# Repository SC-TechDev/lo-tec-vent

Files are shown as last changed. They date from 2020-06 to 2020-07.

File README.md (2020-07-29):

# LoTec Emergency Ventilator Concept - June 6, 2020

This ventilator concept builds on the mechanically actuated Bag-Valve Mask (BVM) designs originally developed at MIT as the [MIT Emergency Ventilator E-Vent](https://e-vent.mit.edu)

The materials provided include engineering drawings, descriptions, photos and videos of designs and proposed production techniques for ventilators Steelcase developed for possible use as part of COVID response actions. Steelcase has not completed the work to validate this design, reviewed these materials with FDA or any other government agency or produced any ventilators. We invite you to use these materials to the extent they are useful in designing and making similar products. However, be advised that these drawings and other materials have not been reviewed by FDA or any other government agency or evaluated for safety or effectiveness for use with any medical condition. We are making these materials available as part of our response to the COVID emergency. Steelcase disclaims any liability for any products made by others using these designs and production techniques. Each user must make their own assessment about the suitability of the design for their particular use.

## Design Goal

The specific goal of this design is to simplify manufacturing and reduce costs and complexity. This is especially relevant in developing countries where servo motors and electronic controls may difficult to procure and maintain. We replaced the servo motor, control board, and electronic user interface with a simple speed-controlled DC motor and adjustable mechanical linkages. This design consists of a standard windshield wiper motor or equivalent connected to a series of mechanical linkages. The steel linkages are assembled with common screws, pins and bearings. The entire unit can be built with standard metal fabrication processes. We improved the user interface with 3D printed handles and covers.

## Proof Of Concept

The following information describes the operation of the ventilator. A prototype was built to prove the concept of the adjustable mechanical linkage. This design is not ready for production or implementation. It does, however, prove that the linkages delivered the desired performance requirements and that the user controls can be simple and intuitive. Further refinement of the design is required to improve durability, manufacturability, and reliability.

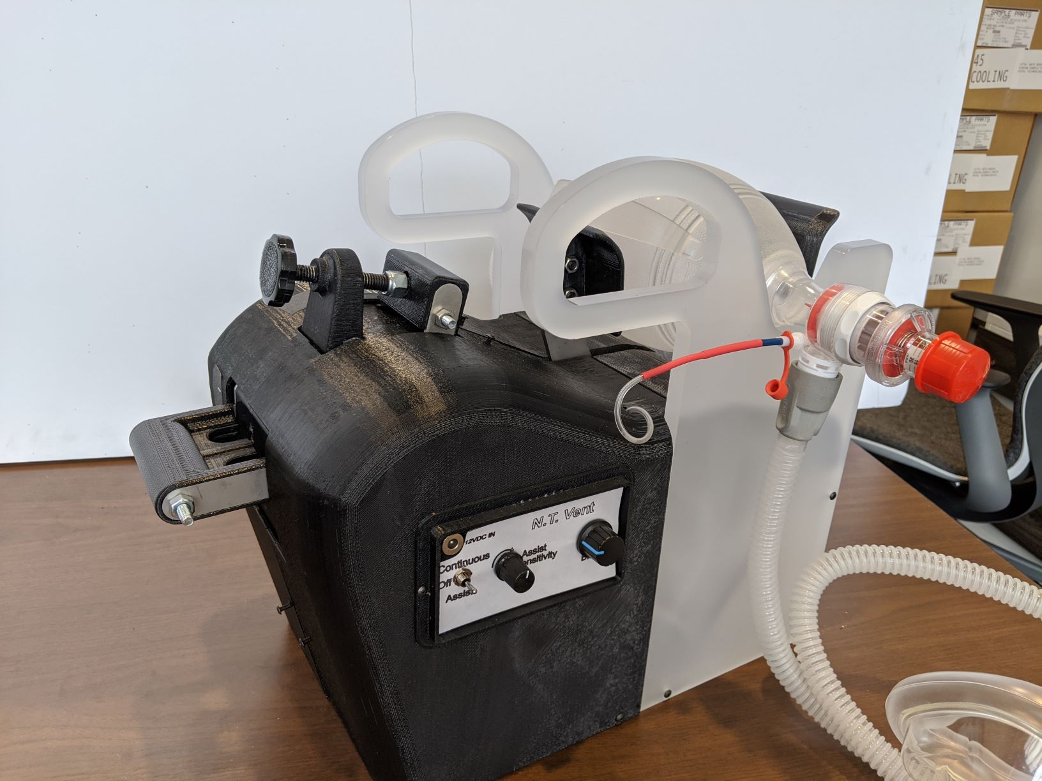
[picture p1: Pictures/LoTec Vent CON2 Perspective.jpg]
LoTec Vent


## Basic Function

Two paddles are used to compress the bag, these paddles are geared together to act in concert as was the MIT E-Vent. A six-bar mechanism was developed to drive the paddle movement. The first bar is the rotating lever mounted to the motor. The second bar is the motor push rod. The third bar is the paddle push rod. The fourth bar is the one of the two paddle supports. The fifth bar is a control arm connected to the motor push rod / paddle push rod joint on one end and fixed to ground on the other end (point A – more about how this pivot point is fixed in place later). The sixth bar is the ground plate.

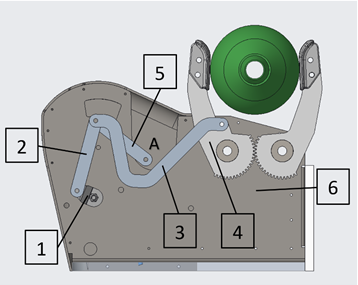
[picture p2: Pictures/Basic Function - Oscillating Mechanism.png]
Oscillating Mechanism


The paddles sweep through a sinusoidal arc as the motor turns. The range of motion, maximum opening angle, and minimum closing angle of the paddles are all controlled by the position of the point A of the control arm.

An automotive windshield wiper motor was used to drive the oscillation. The prototype used a replacement motor for a 1983 Jeep CJ7. PN #REPJ361101. The motor speed was controlled with a pulse width modulated DC speed control module PN CCM5D. Other devices could be used to drive the ventilator. The prototype was noticeably underpowered at slow speeds with this motor and controller so additional work is required to select the appropriate motor, controller and power source.

## Basic Function - User Controls

Two levers are provided for the clinician to adjust the TV and I/E ratio. These levers are part of a 5-bar mechanism that sets the appropriate position for point A. This 5-bar mechanism consists of the two user operated levers, one for TV (1) and one for I/E ratio (2), each pivotally connected to the ground plate (3), and two links (4,5) that determine the position of point A.

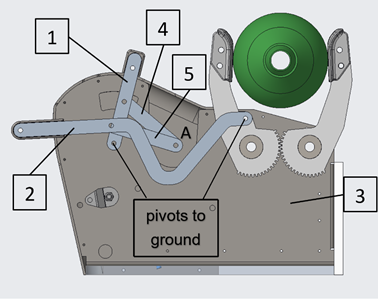
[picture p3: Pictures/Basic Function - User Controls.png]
User Controls


The control levers are moved to the desired position by the clinician and locked into place relative to the ground plate. Indicators on the ground plate will display the selected TV or I/E ratio. The control levers can be adjusted while the ventilator is operating and the change in function observed.
The two control levers operate independently. As the TV is adjusted, the I/E ratio will remain unchanged. As the I/E ratio is adjusted, the TV will remain unchanged.

Once the control levers are locked into place, point A is held fixed to the ground plate at the desired location. This position then serves as the pivot point A for the oscillating mechanism determining the range of motion of the ventilator paddles.

A CAD model of the prototype ventilator is provided in this post to clearly show the linkage connections and arrangement of parts to make a functioning unit. The principles of operation described here may be implemented in other ways, potentially further simplifying manufacturability.

## Ventilator Performance

The minimum closing angle of the paddles determines how far the Ambu-Bag is compressed, and the amount of air delivered to the patient (Tidal Volume). The maximum opening angle affects the inhalation / exhalation time ratio (I/E ratio). The user controls previously described determine the range of motion of the paddles. The four pictures below show the user controls at the extremes of adjustment and the associated performance limits of the ventilator. (Notice the position of point A in each of the pictures.)

&nbsp;&nbsp;&nbsp;&nbsp;&nbsp;&nbsp;&nbsp;&nbsp;&nbsp;&nbsp;&nbsp;&nbsp;Tidal Volume (TV) between 200ml and 800ml

&nbsp;&nbsp;&nbsp;&nbsp;&nbsp;&nbsp;&nbsp;&nbsp;&nbsp;&nbsp;&nbsp;&nbsp;I/E ratio between 1 and 3

&nbsp;&nbsp;&nbsp;&nbsp;&nbsp;&nbsp;&nbsp;&nbsp;&nbsp;&nbsp;&nbsp;&nbsp;Breaths Per Minute (BPM) controlled by the motor speed (rpm)

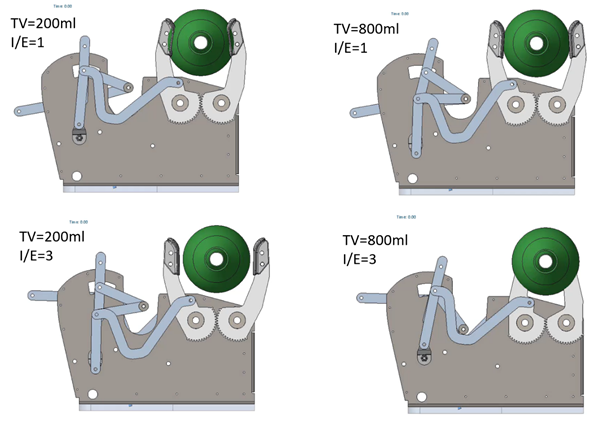
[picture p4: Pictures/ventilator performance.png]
Ventilator Performance


## Credits

I’d like to thank [Steelcase Inc.](https://www.steelcase.com) for supporting the work to develop and build this ventilator concept. Steelcase’s generous access to the model shop and engineering talent during the early days of the pandemic, when a shortage of ventilators was a mounting concern, was critical to its development. As more firms ramped up production of traditional design ventilators, the team shifted to reduce the technological burden of current designs and focus on purely mechanical solutions. I hope that the Lo Tec Vent is an inspiration to someone to further develop and save lives.

## Engineering Team

Thanks to the following:

Gordy Peterson, Nicholas Krupansky, and Nick Deevers – all Steelcase Engineers

Future Contact: Kurt Heidmann kheidman@steelcase.com

## License

MIT modified license:

Permission is hereby granted, free of charge, to any person obtaining a copy of this ventilator design and associated documentation files (the "Ventilator"), to deal in the Ventilator without restriction, including without limitation the rights to use, copy, modify, merge, publish, distribute, sublicense, and/or sell copies of the Ventilator, and to permit persons to whom the Ventilator is furnished to do so, subject to the following conditions:

THE VENTILATOR IS PROVIDED "AS IS", WITHOUT WARRANTY OF ANY KIND, EXPRESS OR IMPLIED, INCLUDING BUT NOT LIMITED TO THE WARRANTIES OF MERCHANTABILITY, FITNESS FOR A PARTICULAR PURPOSE AND NONINFRINGEMENT. IN NO EVENT SHALL THE AUTHORS OR COPYRIGHT HOLDERS BE LIABLE FOR ANY CLAIM, DAMAGES OR OTHER LIABILITY, WHETHER IN AN ACTION OF CONTRACT, TORT OR OTHERWISE, ARISING FROM, OUT OF OR IN CONNECTION WITH THE VENTILATOR OR THE USE OR OTHER DEALINGS IN THE VENTILATOR.

[Full License](License.md)

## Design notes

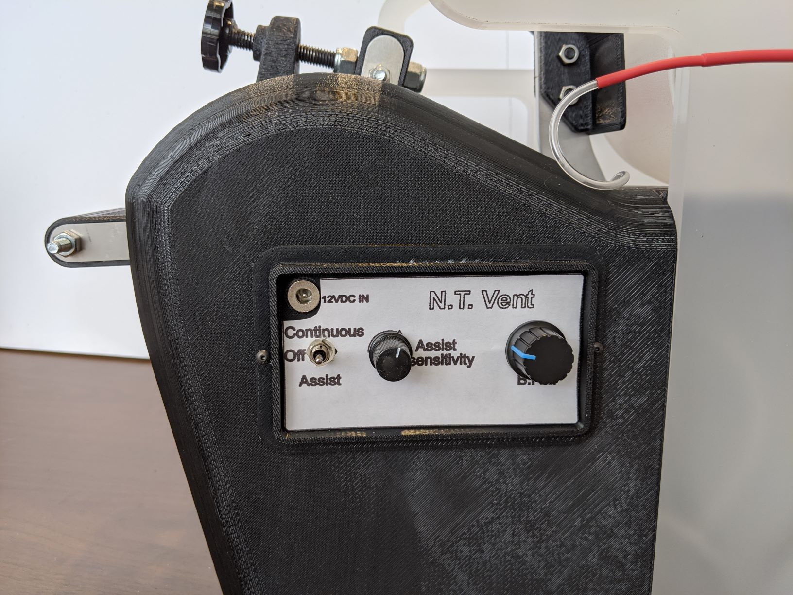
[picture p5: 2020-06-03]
Pictures/LoTec Vent CON2 Motor Control Interface.jpg

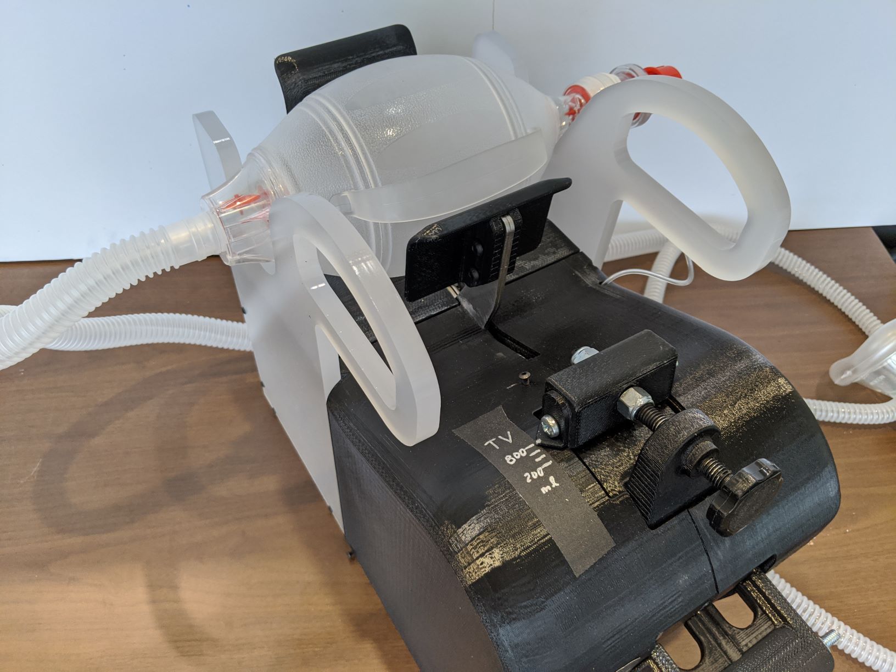
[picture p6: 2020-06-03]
Pictures/LoTec Vent CON2 Top View.jpg

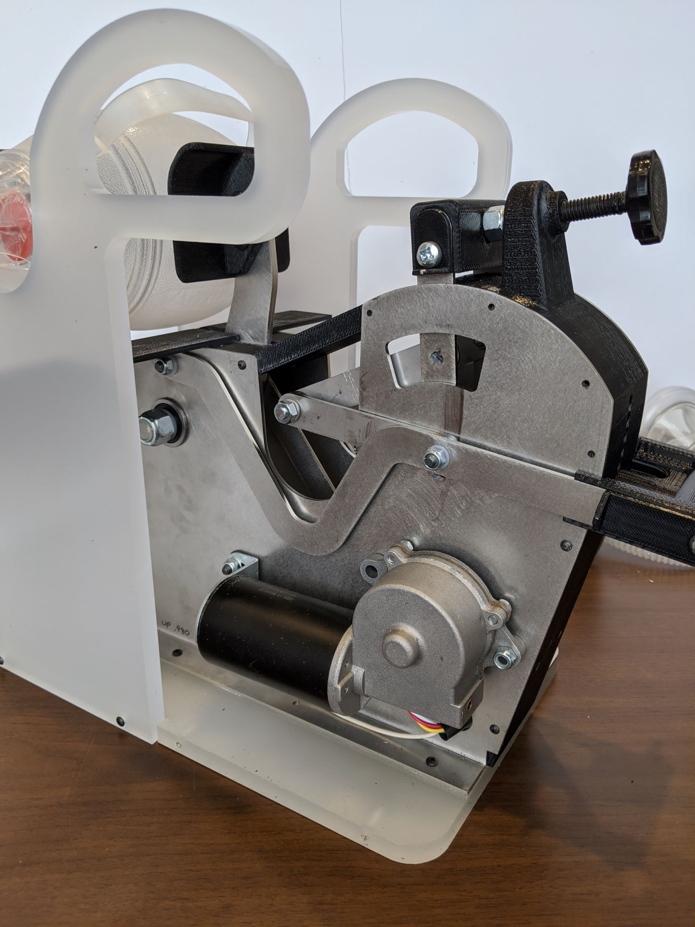
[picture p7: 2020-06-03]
Pictures/LoTec Vent CON2 No Covers.jpg

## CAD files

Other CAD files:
CAD Files/LoTec Vent CON2.f3z
